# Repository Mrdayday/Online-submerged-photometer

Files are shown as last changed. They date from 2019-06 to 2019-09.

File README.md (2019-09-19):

<p align="center">

</p>

## What is this component for?
Its part of the FermenTUM project. This is a photometer for submerged use inside a biological reactor during fermentation.

## About us and the project
We are a group of students from the Technical University of Munich. In the context of a module at our university the following project was created. It is a part of the FermenTUM project. The aim is to build a low-budget bioreactor for use in an internship. The students should learn the basic functions of this machine via a very simple construction. The main difficulty is the size of the container used. It is a [GLS 80® by Schott/Duran](https://www.duran-group.com/uploads/tx_fedownloads/GLS80_A5_E_01.pdf).

## How to use the informations in this Git
For programming the Arduino IDE was used if it is not installed on your device jet you can get it [here](https://www.arduino.cc/en/Main/Software). The [software](https://github.com/Mrdayday/Online-submerged-photometer/tree/master/Software) is in the folder of the same name. Just upload it to the Arduino that you want to use.(We used an [Arduino Nano](https://www.arduino.cc/en/Guide/ArduinoNano))

The wiring and soldering can be seen in [here](https://github.com/Mrdayday/Online-submerged-photometer/blob/master/Wiring.md).

There are data sheets of the used parts and a section where you can see the prototype work. Please notice that this section is not functional.

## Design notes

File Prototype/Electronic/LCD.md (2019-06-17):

The photometer should also work as an standalone. (No master)
For that reason we need a Display to show the Data.
I was running some tests with the LCD 1602 HD44780 Display from Makershop.de shortly. But so far it is not working. I tried to run the code with a pre-soldered version of the Display with an I2C HD44780 module, but was not able to display anything so far.
The code was from the [LiquidCrystal_I2C](https://github.com/johnrickman/LiquidCrystal_I2C) and the [I2CScanner Libary](https://github.com/luisllamasbinaburo/Arduino-I2CScanner).

The Problem with the Dysplay may be caused by some badly soldered parts and some oxidation on the Bord like shown in the picture below.
<p align="center">
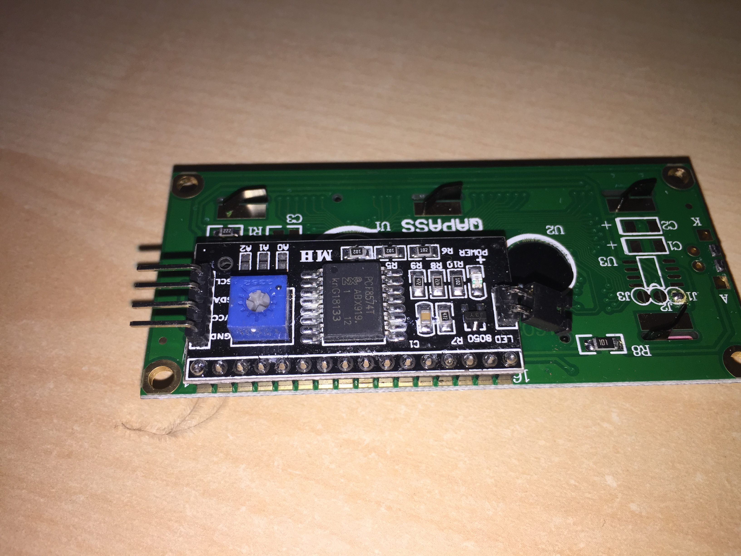
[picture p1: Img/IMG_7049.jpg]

</p>

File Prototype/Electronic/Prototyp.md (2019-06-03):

# Initial Wireing

At the beginning of the projekt the aim was to build a simple photomether. To achieve this we took a Light sensor, in our term the TSL2591 from adafruit, and a LED. 
We wired everthing together like shown in the picture.
<p align="center">
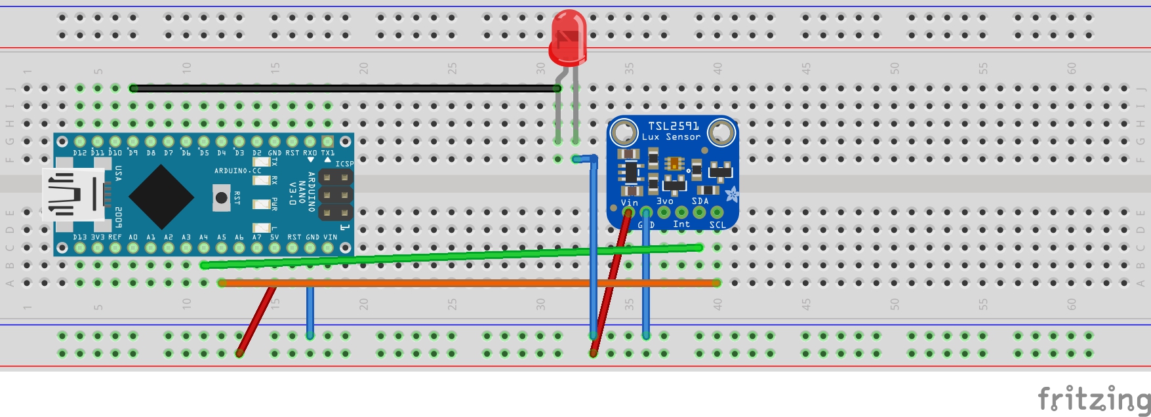
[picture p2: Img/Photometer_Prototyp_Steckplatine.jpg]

</p>
With this setup it was possible to set the brightness of the LED to a predicted level.

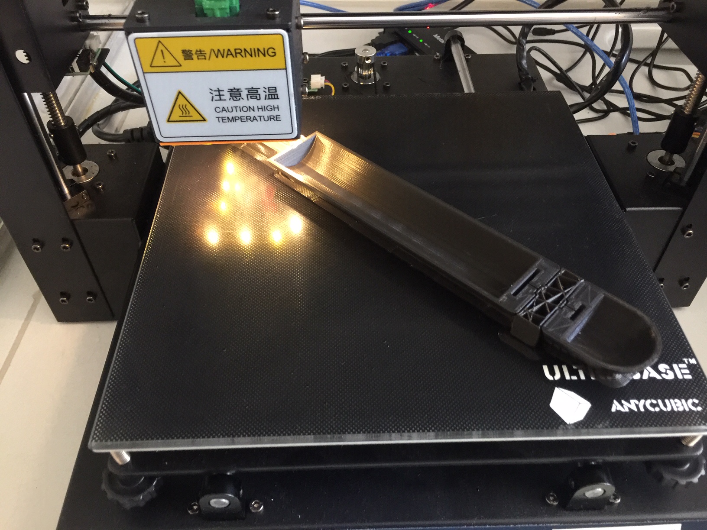
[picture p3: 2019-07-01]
Img/Photometer-huge.jpg

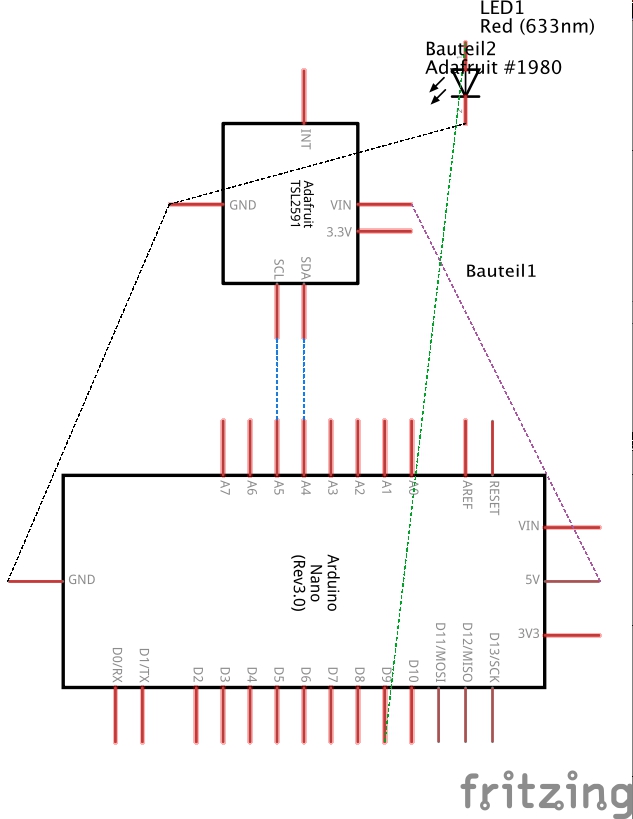
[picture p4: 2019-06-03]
Img/Photometer_Prototyp_Schaltplan.jpg

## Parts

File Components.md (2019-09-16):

This is a list of the bought components:

<table>
<thead>
<tr>
<th>Component</th>
<th>Shop</th>
</tr>
</thead>
<tbody>
<tr>
<td>Sensor TSL2591</td>
<td>https://www.adafruit.com/product/1980</td>
</tr>
<tr>
<td>LED</td>
<td><a href="https://www.leds.de/osram-oslon-ssl-150-smd-led-mit-10x10mm-platine-gelb-593nm-33990.html">Leds.de</a></td>
</tr>
<tr>
<td>LCD1602 display</td>
<td>https://www.makershop.de/display/lcd-tft/lcd1602-blau/</td>
</tr>
<tr>
<td>Arduino nano</td>
<td>https://www.makershop.de/plattformen/arduino/arduino-nano-atmega328p-geloetet/</td>
</tr>
<tr>
<td>PLA</td>
<td>https://www.innofil3d.com</td>
</tr>
<tr>
<td>PVA</td>
<td><a href="https://www.amazon.de/Renkforce-Filament-1-75mm-Transparent-500g/dp/B073JYMLZJ/ref=sr_1_1?__mk_de_DE=ÅMÅŽÕÑ&keywords=renkforce+pva&qid=1568635718&s=ce-de&sr=1-1-catcorr">Amazon (Renkforce)</a></td>
</tr>
<tr>
<td>Glue</td>
<td><a href="https://www.obi.de/lackreparatur-karosseriereparatur/presto-kunststoffspachtel-250-g/p/6636450">Obi</a></td>
</tr>
<tr>
<td>Microscope slides</td>
  <td><a href="https://www.marienfeld-superior.com/information-about-our-microscope-slides.html">Marienfeld</a></td>
</tr>
<tr>
<td>RS485 converter</td>
<td><a href="https://www.ebay.de/sch/i.html?_odkw=Max+485&_osacat=0&_from=R40&_trksid=p2045573.m570.l1313.TR4.TRC0.A0.H0.XMax485.TRS0&_nkw=Max485&_sacat=0">Ebay</a></td>
</tr>
</tbody>
</table>

And a list of the used equipment:

<table>
<thead>
<tr>
<th>Apparatus</th>
<th>Shop</th>
</tr>
</thead>
<tbody>
<tr>
<td>Anicubic i3 Mega</td>
<td>
<a href="https://www.amazon.de/Anycubic-größerer-Druckgröße-Touchscreen-Filament/dp/B06XDFQ3LR/ref=sr_1_5?__mk_de_DE=ÅMÅŽÕÑ&crid=3QMVYAA6NFT6H&keywords=anycubic+i3+mega&qid=1568634754&s=gateway&sprefix=anycub%2Caps%2C159&sr=8-5">Amazon</a>
</td>
</tr>
<tr>
<td>Ultimaker S5</td>
<td>https://ultimaker.com/3d-printers/ultimaker-s5</td>
</tr>
<tr>
<td>Soldering station</td>
<td>https://www.weller-tools.com/we1010na/</td>
</tr>
</tbody>
</table>

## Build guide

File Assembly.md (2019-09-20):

First you should start printing all of the things. The photo unit is quite difficult to print with a "singel nozzled" printer due
to the hard to remove support structure. If you have the posibility to use a two nozzled printer you can print a water-soluble
support structure with PVA. The result is shown in the Picture.

<p align="center">
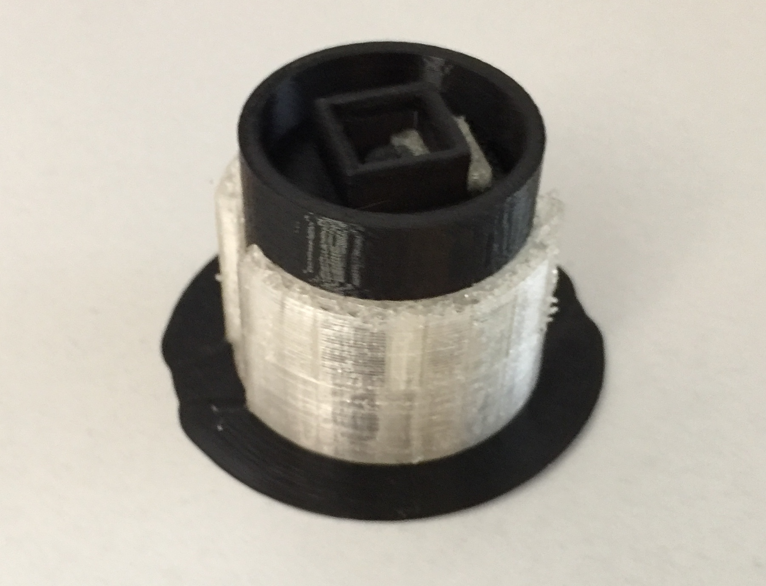
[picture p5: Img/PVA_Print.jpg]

<p>

Once you have printed all parts you can start assambling them. You can assable them all from the bottem to the top if you want.
There is one part missing at the bottem of the submerged part.
We used a half sphere of steel to get rid of the heat produced by the LED. So it would be good to get one of these or somthing
else of equal thermal conductivity and connect it with thermal paste. All other things you can find [here](https://github.com/Mrdayday/Online-submerged-photometer/blob/master/Components.md)

<p align="center">
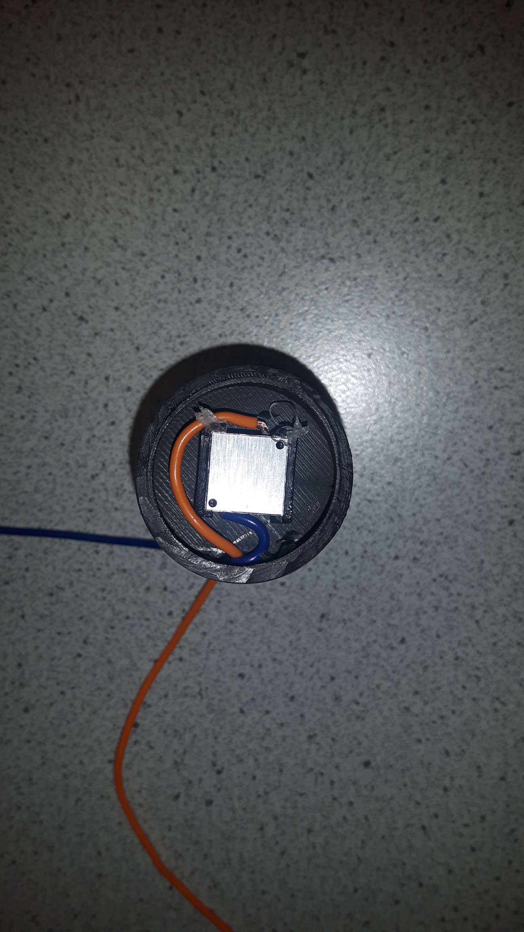
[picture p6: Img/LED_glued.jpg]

<p>

There is a high chance that you will get inaccurate results if you let the LED heat up. Next step is to connect the wires to 
the light source and push them throug the tiny tunnel on the side. Now glue it together and put fix the glass panels in the frames.

<p align="center">
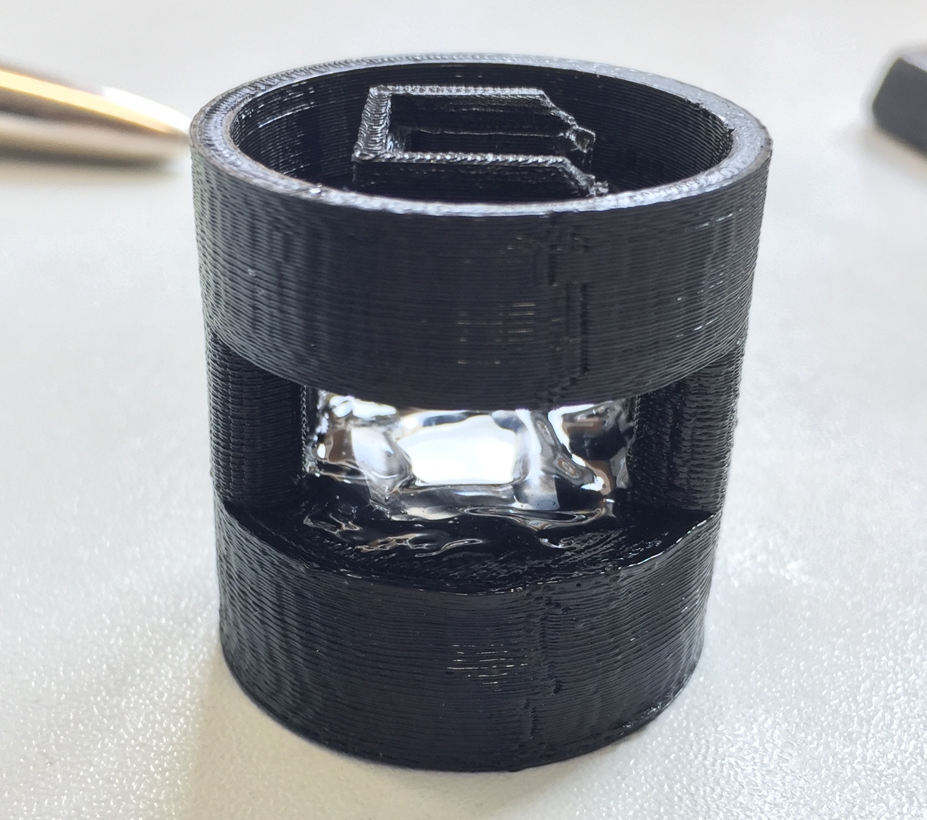
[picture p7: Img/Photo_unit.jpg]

<p>

Now it might be useful to plug everything to the [breadboard](https://github.com/Mrdayday/Online-submerged-photometer/blob/master/Wiring.md) and search for the perfect place for the sensor to get the highes value at the busarry(0).
If you find it glue the sensor and solder the cables.

<p align="center">
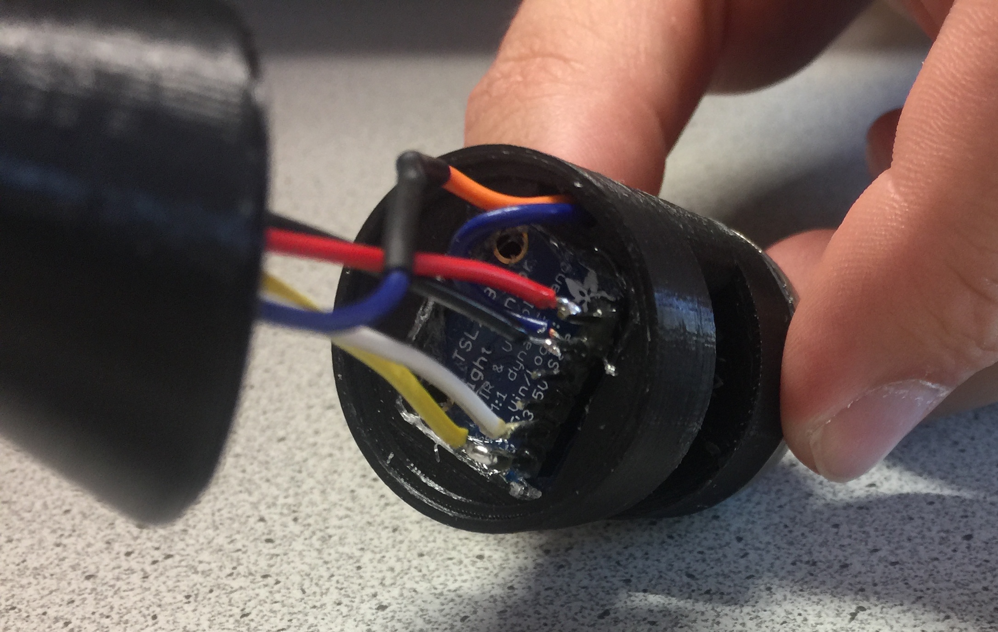
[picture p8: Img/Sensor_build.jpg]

<p>

Now connect the neck of the submerged part and lead the wires to the top. We used hot glue all the time. The result should look like this:

<p align="center">
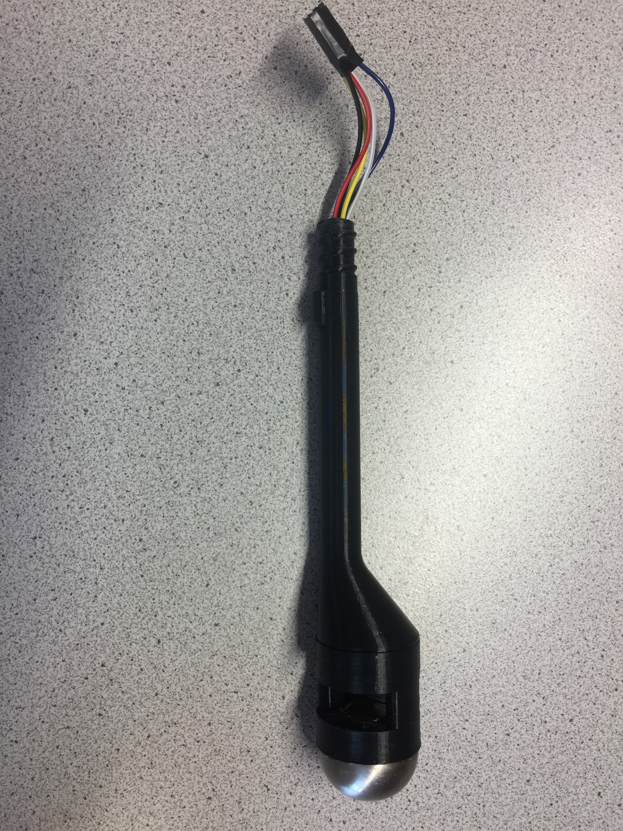
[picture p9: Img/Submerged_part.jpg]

<p>

Now you shold built the stripboard. It is a lot of soldering, but worth it. You can get rid of a lot of cabels, that tend to brake or unplug and last but not least it looks better.

<p align="center">
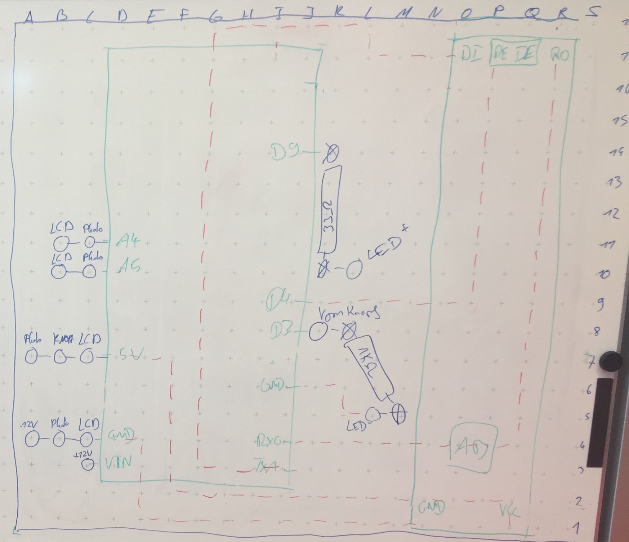
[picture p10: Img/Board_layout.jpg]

<p>
  
<p align="center">
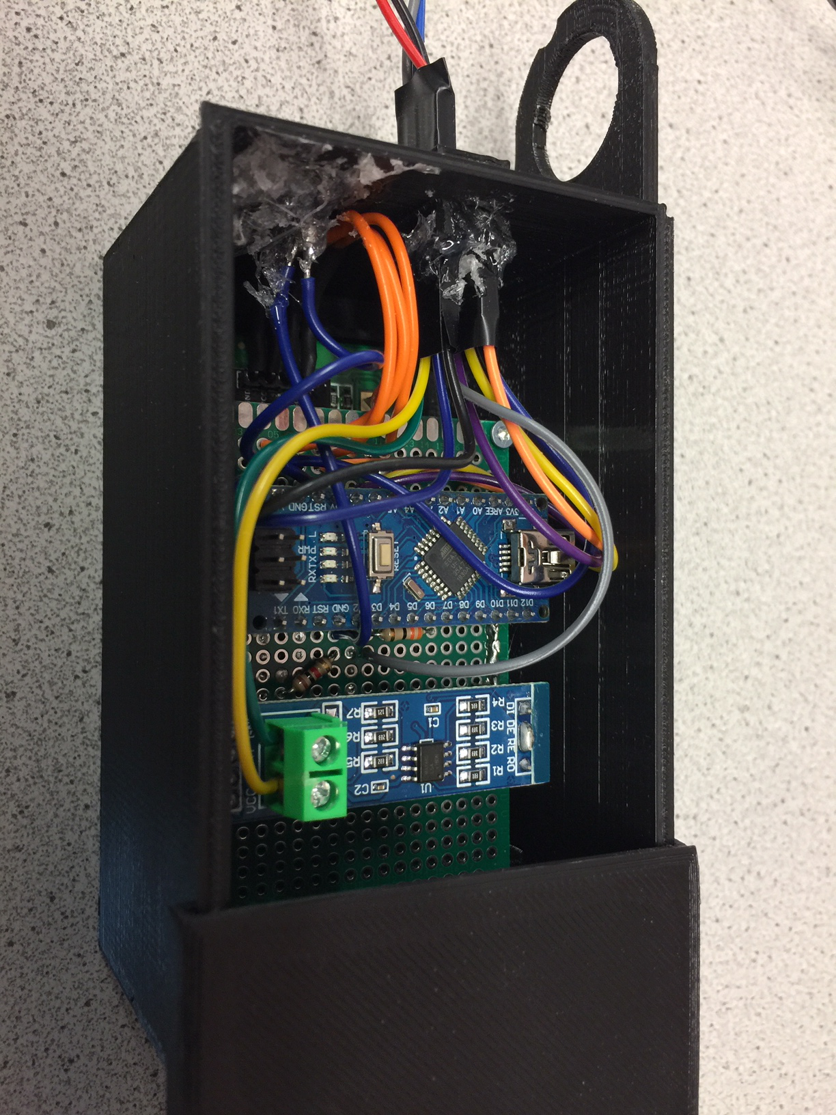
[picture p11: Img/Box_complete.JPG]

<p>

Now solder everthing to the stripboard. Everthing that leaves the box sould use a jumperwire connected to the sideslots of the box.
This includes everthing that is connected to the submerged part (5 cabels), the bussystem (2 cabels) and the 12 V powersuply (2 cabels).
Attach the display and the board to the box. Glue a microscope slide as a display protection to the front, if you want. 

Everything should be ready for commissioning. Attach the box to the reaktor cover and tighten the locknut in the right position.

<p align="center">
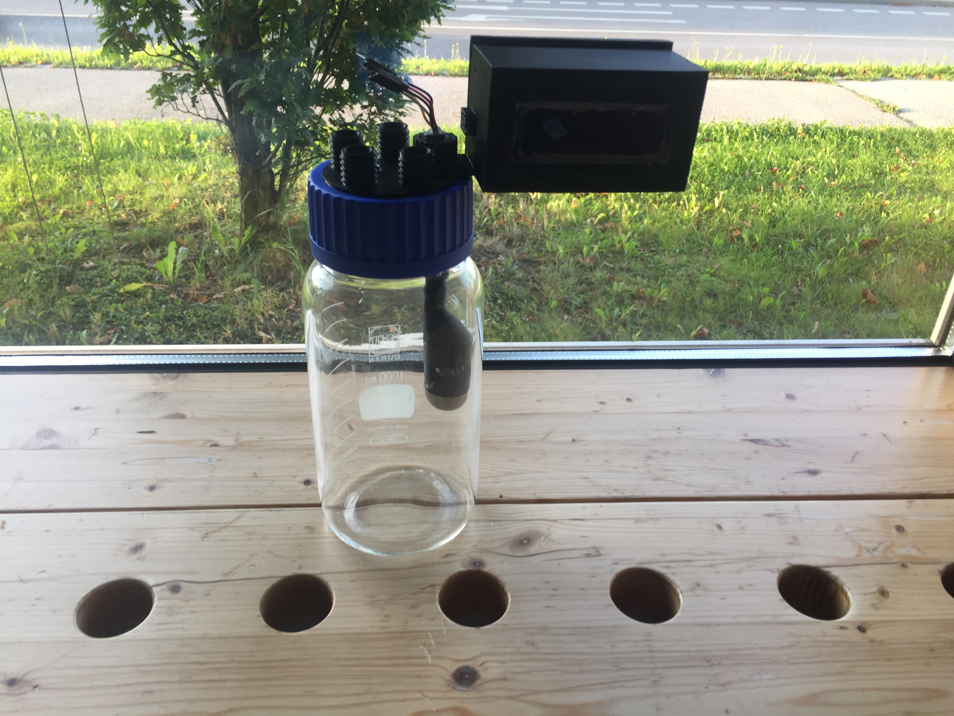
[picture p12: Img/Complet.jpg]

<p>

Ready!!!

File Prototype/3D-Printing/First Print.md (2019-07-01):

For our first steps with 3D printing we used the Anycubic I3 Mega printer. The 3D modeling software was Autodesk Inventor since we lerned it in university. We exported the documents to .stl format and opend them in Cura for slicing. For first prints we useed PLA because it is quite esay to print. Our settings for the "9-gag-logo-cube" were a layer hight of 0.2 and an infill of 20%. The nozell tempreture was 200°C and we sat the bed temprature to 60°C. With these settings we maneged to get a very good print like you will see in the picture below.

<p align="center">
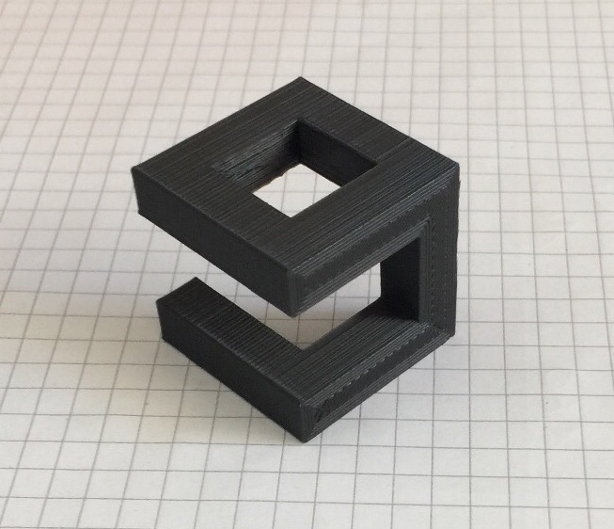
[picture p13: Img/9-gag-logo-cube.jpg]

</p>

The next step was to print a tube or more of a ring with the Anycubic. The problem was, that we wanted to print it standing upwards, so the tention, of the fuluid dynamics inside the reaktion camber, do not breake the zylinder. The exacting force should not be along with the filaments layers. We needed a few prints to achieve this. We had some truble with the suport structures. The main topic with this issue was to find the right angle to start with the suport structures.

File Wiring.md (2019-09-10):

<p align="center">
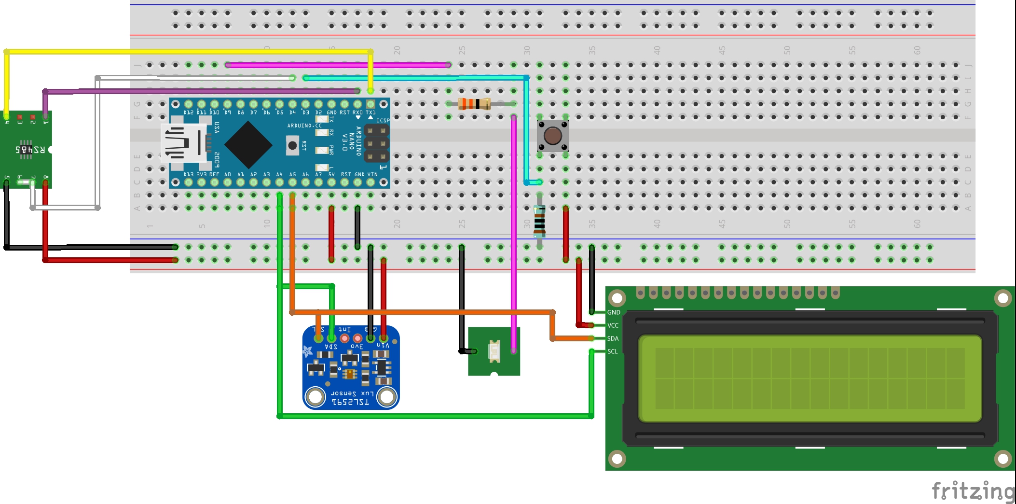
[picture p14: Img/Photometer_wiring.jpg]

</p>

<p align="center">
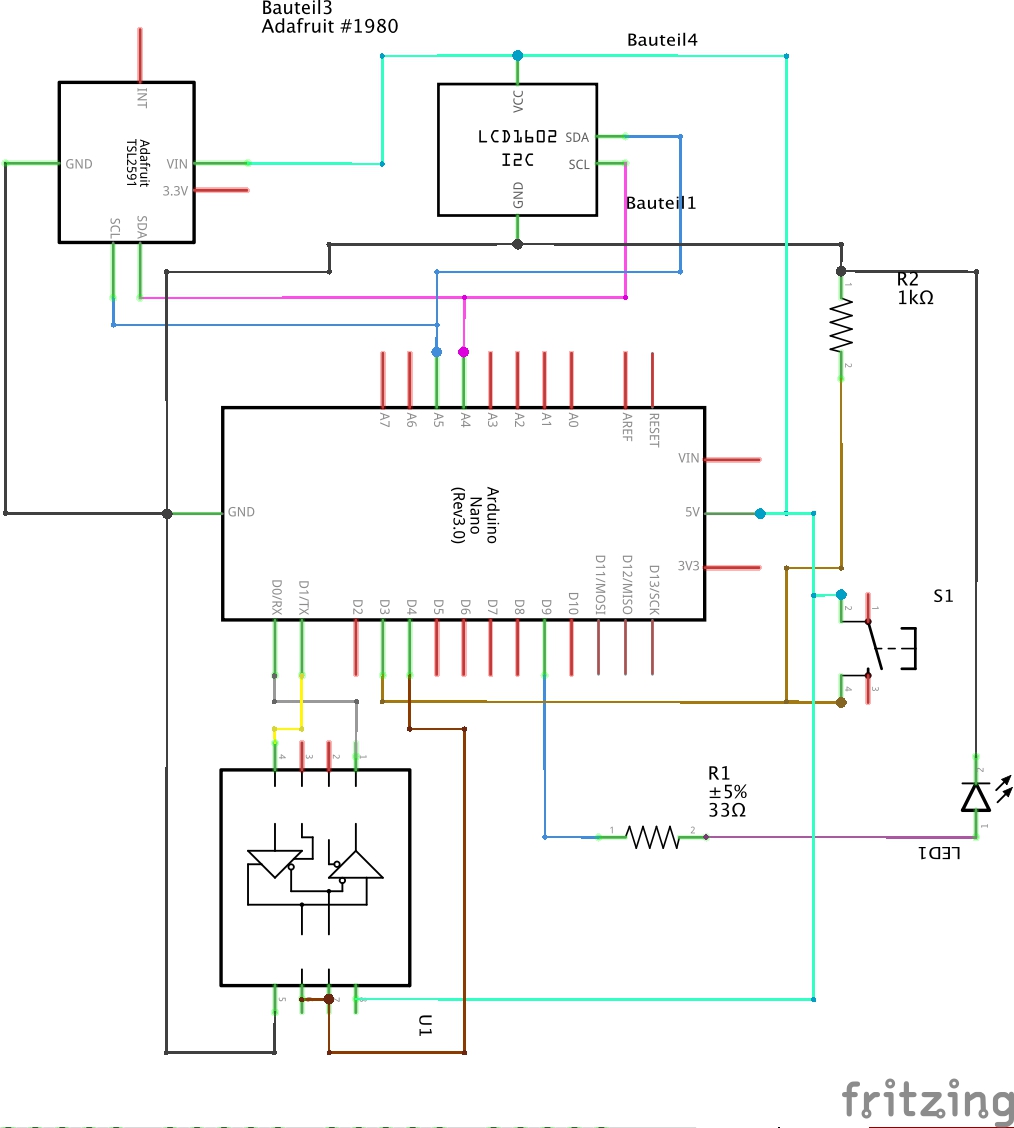
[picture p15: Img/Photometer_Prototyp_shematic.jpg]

</p>

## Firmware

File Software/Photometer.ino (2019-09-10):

/* TSL2591 Digital Light Sensor */

//include Libarys
//Adafruit basic libary
#include <Wire.h>
//Sensor
#include <Adafruit_Sensor.h>
#include "Adafruit_TSL2591.h"
//Modbus libary (Modbus Master-Slave library for Arduino by smarmengol(Github)
#include <ModbusRtu.h>
//Libary for the LCD-Display
#include <LiquidCrystal_I2C.h>

LiquidCrystal_I2C lcd(0x27,20,4); // set the LCD address to 0x27 for a 16 chars and 2 line display (Code by YWROBOT/Ec-yuan)

Adafruit_TSL2591 tsl = Adafruit_TSL2591(2591); // pass in a number for the sensor identifier (for your use later)

// Variabls
// Timers
unsigned long LooptimeMeasurement;
unsigned long LooptimeLCD;
// Pinnumber for Modbus
#define TXEN  4 
//Modbusobject
Modbus slave(1,0,TXEN);
//Array for Modbus
uint16_t photodata[3]={0,0,1};
/*
 * photodata[0]=Value now
 * photodata[1]=currentoutput
 * photodata[2]=blank
 */
//define Pins
//Pin for the Blankbutton
#define blankPin 3
// Pin für LED
#define LEDPIN 9
// Time intervals
int intervalltimeMeasurement=500;
int intervalltimeLCD=10000;
// Array for raw data
uint16_t data[100];
// conter1 for the data array
int i;
//Chekpoint variable to see if array has already reached 100 values
bool over100;
//variable to see if a blank given once
bool blankgiven;
//For calculation of sums in a loop
unsigned long sum;
int currentOutput;

//    Configures the gain and integration time for the TSL2591

void configureSensor(void)
{
  //Sets the the gain of the sensor to medium
  tsl.setGain(TSL2591_GAIN_MED);      // 25x gain
  
  //integration time set to 500 milliseconds
  tsl.setTiming(TSL2591_INTEGRATIONTIME_500MS);


}

void bootScreen(void)
{
  //initialize
  lcd.init(); 
  lcd.backlight();
  // infomation on display while booting
  lcd.setCursor(0,0);
  lcd.print("FermenTUM|PhoTUM");
  lcd.setCursor(0,1);
  lcd.print("Lukas+Max+Jan");
}

void setup(void) 
{
  // set bauderate to 19200 for Slave master communication
  slave.begin(19200); 
  //Bootscreen on LCD
  bootScreen();
  /* Configure the sensor */
  configureSensor();
  // get a starttime
  LooptimeMeasurement = millis();
  LooptimeLCD = millis();
  //set counter to 0
  i=0;
  int currentOutput=1;
  //inizilase LEDpin
  pinMode(LEDPIN,OUTPUT);
  digitalWrite (LEDPIN,1);
  //inizialase BlankButtonPin
  pinMode(blankPin,INPUT);
  //chekpoint Variable
  //variable to see if array is full
  over100=0;//or byte
  //variable to see if a blank given once
  blankgiven=0;
}

//simple read was used to get the intensety of visible light

void simpleRead(void)
{
  // Function to get intensety of visible light
  uint16_t x = tsl.getLuminosity(TSL2591_VISIBLE);
}


void loop(void) 
{ 
  // wait vor the preset time
 Start: slave.poll(photodata,3);
  if (millis()>LooptimeMeasurement + intervalltimeMeasurement){
    // get the intensety of the light at the sensor
    int16_t x = tsl.getLuminosity(TSL2591_VISIBLE);
    if (x<0) goto Start;
    photodata[0]=x;
    // reset counter if over hundret to get an array of hundret values
    if (i>=100){
      i=0; //to dont get a to high counter
      //to know if array was filled once
      over100=1;
    }
    
    if (over100==1){//Move each entry one position forward.
      for(int k=0; k<99;k++){
        data[k]=data[k+1];
      }
      data[99]=x;
    }
    else{//write the value into the array
      data[i]=x;
    }
  
    //data for the output is the mean of the 100 values
    //was done to get rid of noise in the data
    if (over100==1){
      for (int k=0; k<100;k++){
        //sum up the whole array
        sum=sum+data[k];
      }
      currentOutput=sum/100;
      sum=0;
    }
    else{
      for (int k=0; k<i;k++){
        sum=sum+data[k];
      }
      currentOutput=sum/i;
      sum=0;
    }
    //write averaged value into array
    photodata[1]=currentOutput;
    //raise the counter
    i++;
    //get the Starttime of the next Loop
    LooptimeMeasurement = millis();
  }
  /*

 
  Spaceholder for The bus system


  */
  if (photodata[2]!=1) blankgiven=1;

  if (digitalRead(blankPin)==1){
    blankgiven=1;
    photodata[2]=photodata[1];
  }
  
  
  if (millis()>LooptimeLCD + intervalltimeLCD){
    //display information on the LCD display
    lcd.clear();
    lcd.setCursor(0,0);
    lcd.print("NOW:");
    lcd.setCursor(4,0);
    lcd.print(currentOutput);
    LooptimeLCD=millis();
    if (blankgiven==1&&photodata[2]!=0){
      //calculate Trasmission
      float transmission=(float)photodata[1]/(float)photodata[2];
      lcd.setCursor(0,1);
      lcd.print("Transmis.:");
      lcd.setCursor(10,1);
      lcd.print(transmission*100,1);
      lcd.setCursor(15,1);
      lcd.print("%");
    }
  }
}

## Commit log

2019-06-03 Create First Print.md
2019-06-06 Datasheet for the used sensor
2019-07-01 Update First Print.md
2019-07-01 Add files via upload
    Pictures of 3D printed parts
2019-09-10 Rename 3D-Printing/First Print.md to Prototype/3D-Printing/First Print.md
2019-09-10 Create LED.pdf
    Added the datasheet of the lightsource
2019-09-19 add prints
    [Box-Bildschirm.v3.stl, Version 3 Mitte.stl, Version 4 Hals.ipt, Version 4 Mutter Halterung.ipt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]
2019-09-20 Update Assembly.md
    Spelling improvement
2019-09-20 Add files via upload
    New top part of the photometer
    [Version 4 Hals.ipt, Version 4 Hals.stl]
